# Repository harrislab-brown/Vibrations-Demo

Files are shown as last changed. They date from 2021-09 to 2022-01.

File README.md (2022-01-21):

# Vibrations-Demo
The goal of this project is to create a reconfigurable laboratory kit that is designed to be used as part of a first undergraduate course in mechanical vibrations. The kit was designed to be low-cost and allow for a series of laboratory experiments to be performed remotely. Using a common set of core hardware and software, five laboratory experiments are detailed and can be performed to supplement many of the major topics traditionally encountered in a first vibrations course. 

This repository contains:
1. Assignments: Sample student lab assignments which detail how each demo might be used in the classroom. Each assignment subfolder also contains a video of each demo.
2. CAD files: All files of components needed to be manufactured using 3D printing are provided in both step and stl format. 
3. Laser cut files: All files of components needed to be manufactured by laser cutting are provided in step format.
4. Mechanical drawings: Mechanical drawings of components that need to be manufactured by alternative methods (simple metal working). 
5. Software: All software used in the project (MATLAB GUI, Octave Tone Generator, and Arduino code for accelerometer) are provided. 
6. Vibrations kit assembly guide: A step-by-step guide to assembly and manufacturing of each kit.
7. Vibrations kit BOM: Bill of materials with suggested url for purchasing. 

Additional details on the implementation and motivation can be found at: https://arxiv.org/abs/2110.04668

The documentation in this project is licensed under CC-BY 4.0.
The hardware and software in this project are licensed under CERN-OHL-P.

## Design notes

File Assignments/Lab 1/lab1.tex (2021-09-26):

\documentclass[12pt,letterpaper,english]{article}
\usepackage[T1]{fontenc}
\usepackage[latin9]{inputenc}
\pagestyle{empty}
\usepackage{amsmath}
\usepackage{amssymb}
\usepackage{graphicx}
\usepackage{bm}
\usepackage{multicol}
\usepackage{enumitem}

\usepackage{hyperref}
\hypersetup{
    colorlinks=true,
    linkcolor=blue,
    filecolor=magenta,      
    urlcolor=cyan,
}

\newcommand{\norm}[1]{\lVert#1\rVert}

\makeatletter

\special{papersize=\the\paperwidth,\the\paperheight}

\textwidth6.5in\textheight9in\topmargin-.25in\oddsidemargin0in\evensidemargin0in\parskip5pt\parindent0pt

\usepackage{fancyhdr}
\pagestyle{fancy}
\lhead{Reconfigurable Mechanical Vibrations Laboratory Kit}
\rhead{}

\usepackage{lastpage}

\rfoot{Page \thepage \hspace{1pt} of \pageref{LastPage}}

%\rfoot{\small }
\lfoot{Mechanical Vibrations: Lab 1}

\cfoot{}

\usepackage{babel}

\makeatother

\usepackage{babel}
\begin{document}
\global\long\def\Re{{\rm {Re }}}
 \global\long\def\cL{{\cal L}}
 \global\long\def\sq{{\rm {sq}}}
 \global\long\def\bfx{{\bf x}}
 \global\long\def\bfi{{\bf i}}
 \global\long\def\bfj{{\bf j}}

\begin{center}
\textbf{\large Lab Assignment 1: 1DOF}
\par\end{center}{\large \par}

For this first lab assignment, you will investigate a forced 1 degree of freedom system. The system we will explore is a base excitation problem where a payload is forced by a spring attached to a vibrating base.  Part of the goal of this first assignment will be to help you get familiarized with the shaker setup, housing, and Matlab GUI that will be used for other labs in the future.  

\begin{center}
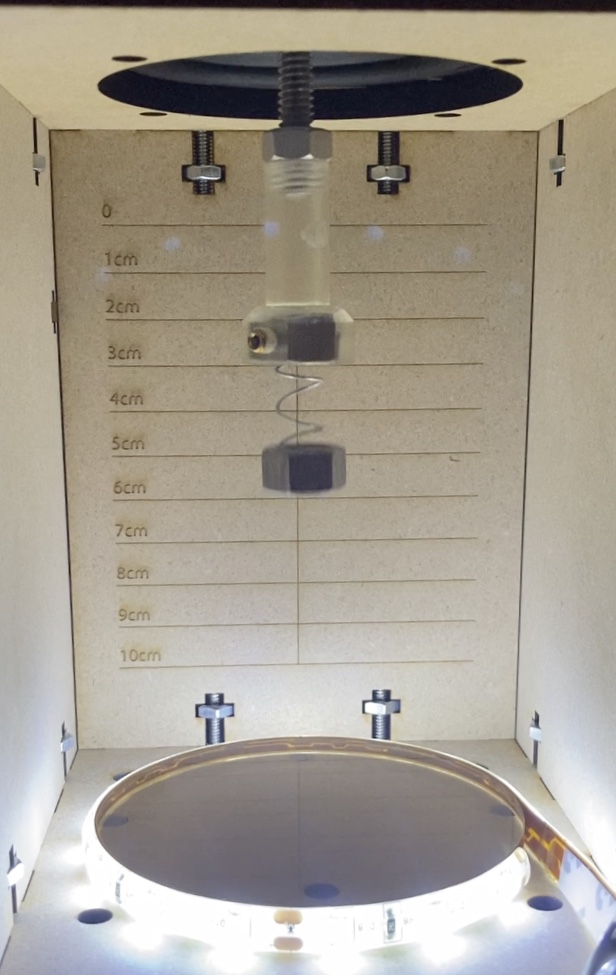
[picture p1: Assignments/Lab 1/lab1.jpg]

\end{center}

\begin{itemize}
\item In the Assembly Guide, first read through and complete the steps in sections A (Housing Assembly), B (Electronics Assembly), C (User Interface), D (Testing the System) to construct the shaker housing, assemble the simple electronic circuit for the shaker and learn to use the GUI.
\item Next read through subsections 1 and 1.1 under section E.  Subsection 1 is a general overview of how to use and assemble parts required for the first demo. Section 1.1 details the specific modifications to the general assembly that are needed for this week's demo. {\it Note that for this demonstration, we will not be using the linear shaft (as described in section E1).}
\end{itemize}

\begin{enumerate}
\item Take a picture of your completed setup.
\item We will first explore the effect of strobing.  For the best effect, the rest of the room should be reasonably dark. To do this, first attach only the nut to the spring (no magnets). Vibrate the speaker at 30Hz with a reasonable amplitude (ensuring that it's not bottoming out!). Then, activate the strobing option on the GUI. Initially, set the strobing frequency offset to 1Hz. Then, explore what happens as the strobing frequency offset is changed to larger or smaller values.  Describe and rationalize observations of the strobing effect you observe and the quantitative influence of the offset.
\item Based on the instructions in E1.1, we will explore the different regimes of forced vibration discussed in class. We will tune the mass of the payload by attaching one or two magnets to the nut. Predict the natural frequency of the three configurations (only nut, one magnet attached, two magnets attached). The spring constant is given by the manufacturer to be around 1050 N/m, while the mass of one nut is approximately 7 g. The mass of one magnet is around 12 g. 
\item We will first investigate the configuration where the nut and one magnet are attached to the end of the spring. Our goal is to use the help of strobing to sweep the frequency space and observe the effect of the driving frequency. For this, we recommend using an offset strobing frequency of 1 or 2 Hz. Start the sweep at around 10 Hz (the speaker is not designed to operate any lower). Then, increase the frequency in 5 Hz steps. As you are doing this, take note of the relative amplitude between the rigid mounting coupler and nut to get a sense of the magnification.  Also take note of the relative phase between the mounting coupler and nut. Continue the sweep in 5 Hz increments until you reach the predicted natural frequency.  You should see the largest amplification around this value since the system is only very weakly damped. Finally sweep beyond the natural frequency until you notice that the nut is almost stationary while the mounting coupler is still visibly vibrating.  Make a qualitative sketch/plot of the motion of the mass and mount as a function of time for three cases (clearly specifying the frequencies chosen): (1) Below the predicted natural frequency, (2) at the predicted natural frequency, and (3) above the natural frequency, again paying particular attention to the relative amplitude and phase of the driving and response.
\begin{itemize} 
\item {\small \underline{Tips:} During the sweep, you may notice that the nut has higher order resonant modes which causes the nut to vibrate side to side. If you encounter these modes, simply skip over that specific frequency (only vertical amplification constitutes the actual resonance we are looking for). 
\item As you sweep, be careful to tune the amplitude slowly so as to avoid the speaker bottoming out (this is when the threading piece glued to the speaker starts hitting the bottom of the speaker and can be easily identified from a clashing sound). As the frequency is increased, the max amplitude of the speaker decreases. Thus you will need to adjust the amplitude value on the GUI as frequency changes. 
\item If the lights start to dim during your sweep, simply reduce the amplitude of the shaker to 0 with the GUI, increase your computer's volume until the lights are at a suitable intensity, then slowly increase the shaker amplitude on the GUI again.
\item If you hear the speaker bottoming out, the fastest way to shutdown the system is to either mute your volume or immediately press the system off button on the GUI. }
\item {\small Ensure that the magnet is properly centered around the nut. This will help minimize any additional side to side vibrational modes. 
\item Be careful when handling the magnets so as to avoid them from snapping together quickly. The best way to remove them from one another once attached is to slide them apart tangentially as opposed to pulling them apart in the normal direction.  }

\end{itemize}

\item Repeat part (d) with no magnet, and finally with both magnets attached. 
\item Provide feedback or ideas (positive and/or areas for improvement) on the setup process and first 1DOF demonstration.  (Optionally) Please also share any other photos or videos you collect!
 
\end{enumerate}

\end{document}

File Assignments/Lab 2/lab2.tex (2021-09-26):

\documentclass[12pt,letterpaper,english]{article}
\usepackage[T1]{fontenc}
\usepackage[latin9]{inputenc}
\pagestyle{empty}
\usepackage{amsmath}
\usepackage{amssymb}
\usepackage{graphicx}
\usepackage{bm}
\usepackage{multicol}
\usepackage{enumitem}

\usepackage{hyperref}
\hypersetup{
    colorlinks=true,
    linkcolor=blue,
    filecolor=magenta,      
    urlcolor=cyan,
}

\newcommand{\norm}[1]{\lVert#1\rVert}

\makeatletter

\special{papersize=\the\paperwidth,\the\paperheight}

\textwidth6.5in\textheight9in\topmargin-.25in\oddsidemargin0in\evensidemargin0in\parskip5pt\parindent0pt

\usepackage{fancyhdr}
\pagestyle{fancy}
\lhead{Reconfigurable Mechanical Vibrations Laboratory Kit}
\rhead{}

\usepackage{lastpage}

\rfoot{Page \thepage \hspace{1pt} of \pageref{LastPage}}

%\rfoot{\small }
\lfoot{Mechanical Vibrations: Lab 2}
\cfoot{}

\usepackage{babel}

\makeatother

\usepackage{babel}
\begin{document}
\global\long\def\Re{{\rm {Re }}}
 \global\long\def\cL{{\cal L}}
 \global\long\def\sq{{\rm {sq}}}
 \global\long\def\bfx{{\bf x}}
 \global\long\def\bfi{{\bf i}}
 \global\long\def\bfj{{\bf j}}

\begin{center}
\textbf{\large Lab Assignment 2: Passive Isolation}
\par\end{center}{\large \par}

Read through section E2 in the Assembly Guide for instructions on what to assemble for this lab. 

First, add about 15 dried beans to the upper platform as shown below.
%
\begin{center}
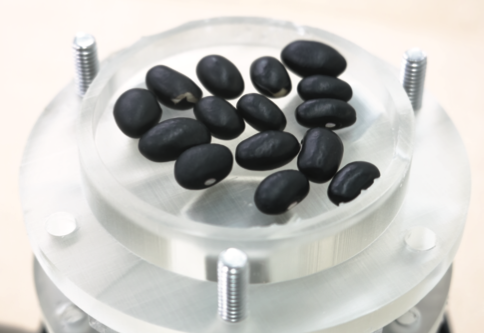
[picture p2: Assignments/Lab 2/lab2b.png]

\end{center}

For this lab, we will explore the effectiveness of a simple passive isolation system. The first configuration (1) contains the upper platform on the passive isolation platform {\it(with the bolts fixed}, shown in the left image below). The second configuration (2) contains the cup placed on the passive isolation rig {\it(without the bolts} so that the springs are free, as in the right image below).

\begin{center}
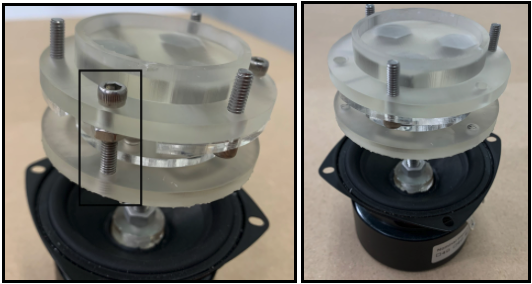
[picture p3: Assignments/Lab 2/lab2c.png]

\end{center}

Set the diving frequency to 120Hz. Note that for the entirety of this demo, the strobing is not needed (but can be experimented with if you would like). Once the shaker starts vibrating, explore configuration (1): rigid support.  Take note of the amplitude at which the beans just begin to move around on the platform. If the amplitude doesn't seem to be high enough, slowly increase the driving amplitude of the speaker until the beans clearly move.  \\

\begin{enumerate}

\item Explore how the intensity of the movement of the beans changes between configuration (1) and (2) under the same driving parameters at 120 Hz.  Take a video of the bean motion for both configurations. 
\item Repeat the above, but this time reducing the driving frequency in 20 Hz steps down to 30 Hz (and resetting the driving amplitude as needed).  
At each frequency, specifically take note as to whether the bean motion appears to be reduced, increased, or stay the same by the inclusion of the springs in configuration (2).  Explain and rationalize your observations.
\begin{itemize}
\item {\small In addition to the bean test, you can also try a ``touch'' test where you gently place your finger on the base and then on the isolation platform.  At each frequency, note how much vibration is transmitted from the base to the isolation platform.}

\end{itemize}

\item Provide feedback or ideas (positive and/or areas for improvement) on the setup process and passive isolation demonstration. 

\end{enumerate}

\end{document}

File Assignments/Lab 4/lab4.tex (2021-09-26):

\documentclass[12pt,letterpaper,english]{article}
\usepackage[T1]{fontenc}
\usepackage[latin9]{inputenc}
\pagestyle{empty}
\usepackage{amsmath}
\usepackage{amssymb}
\usepackage{graphicx}
\usepackage{bm}
\usepackage{multicol}
\usepackage{enumitem}

\usepackage{hyperref}
\hypersetup{
    colorlinks=true,
    linkcolor=blue,
    filecolor=magenta,      
    urlcolor=cyan,
}

\newcommand{\norm}[1]{\lVert#1\rVert}

\makeatletter

\special{papersize=\the\paperwidth,\the\paperheight}

\textwidth6.5in\textheight9in\topmargin-.25in\oddsidemargin0in\evensidemargin0in\parskip5pt\parindent0pt

\usepackage{fancyhdr}
\pagestyle{fancy}
\lhead{Reconfigurable Mechanical Vibrations Laboratory Kit}
\rhead{}

\usepackage{lastpage}

\rfoot{Page \thepage \hspace{1pt} of \pageref{LastPage}}

%\rfoot{\small }
\lfoot{Mechanical Vibrations: Lab 4}
\cfoot{}

\usepackage{babel}

\makeatother

\usepackage{babel}
\begin{document}
\global\long\def\Re{{\rm {Re }}}
 \global\long\def\cL{{\cal L}}
 \global\long\def\sq{{\rm {sq}}}
 \global\long\def\bfx{{\bf x}}
 \global\long\def\bfi{{\bf i}}
 \global\long\def\bfj{{\bf j}}

\begin{center}
\textbf{\large Lab Assignment 4: Multi-DOF Systems}
\par\end{center}{\large \par}

The goal of this demo will be to explore a two degree of freedom system consisting of two springs and two masses. First, read through section E1 (``1 DOF and 2 DOF Assembly'') in the Assembly Guide in order to set up the system.  Note that this setup for this lab is identical to the first lab (1DOF) with the exception of an extra spring and nut added to the assembly. Your final setup should look like the photo below (note that blue guide rod should be attached for this demo for the best results).  

\begin{center}
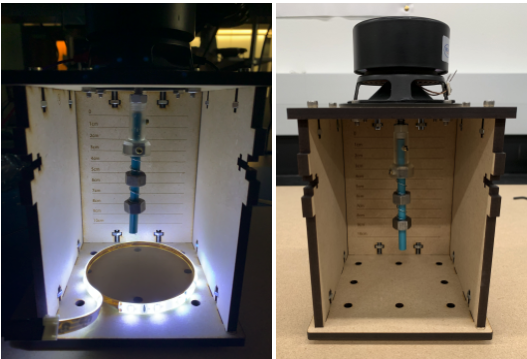
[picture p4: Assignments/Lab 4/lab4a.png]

\end{center}

\begin{enumerate}
\item First, draw a schematic illustrating how you would model the system, labelling all the masses and springs. Note that this can be modeled as a base excitation type problem.  Also clearly label the $x_1$ and $x_2$ coordinates denoting the position of the upper and lower mass, respectively.  
\begin{enumerate}
\item Write down the equations of motion for both masses, then rewrite the system in matrix form. For the purposes of the model, you should assume that the system is undamped, and that the masses and springs are identical.  The spring constant is given by the manufacturer to be around 1050 N/m, while the mass of one nut is approximately 7 g. 
\item Determine the natural frequencies and corresponding mode shapes of the 2DOF system.
\item Lastly, solve for the forced response of the two masses as a function of the driving (i.e. base excitation) frequency.  Plot the frequency response function of the upper mass (mass 1).  Correlate and label the peaks in the frequency response function to the normal modes of the system predicted in the prior part of this problem.  On the same plot, overlay the frequency response function for the 1DOF system from Lab 1 (single spring and nut case).
\item In the 2DOF system, there is also a driving frequency at which the upper mass is predicted to be completely stationary.  Calculate this special frequency.
\end{enumerate}

\item In the experiment, explore driving frequencies from 30Hz to 100Hz in order to experimentally identify the resonant frequencies (and corresponding mode shapes) as well as the special frequency at which the upper mass is nearly stationary.  Setting the strobing frequency to an offset value from the driving frequency will be very helpful for visualizing the relative amplitudes (and for the best effect, turn off the surrounding lights).  Report the experimentally determined frequencies and mode shapes and compare directly to the theoretical predictions from the previous part of this problem.  

\item Lastly, add one additional nut and spring to the end of the chain to create a 3DOF system.  Again by exploring different frequencies under strobing, identify a new qualitative response behavior.  Take a video of one these responses, and include with your assignment.  No calculations are required for this part.

\item Provide feedback or ideas (positive and/or areas for improvement) on the setup process and multi-DOF lab.

\end{enumerate}

\end{document}

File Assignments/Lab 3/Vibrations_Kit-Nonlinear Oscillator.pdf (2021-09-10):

Reconfigurable Mechanical Vibrations Laboratory Kit

### Lab Assignment 3: Nonlinear Oscillator

The goal of this demo will be to investigate the dynamics of a nonlinear oscillator. This system, as depicted below, can be modeled by a Duffing equation where there is a nonlinear spring term in the governing equation.

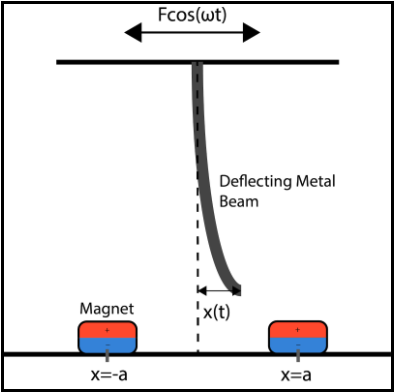
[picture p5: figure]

First, read through section E3 (“Nonlinear Oscillator Demo”) in the Assembly Guide to learn how to modify the existing housing to incorporate the necessary components for this demo. The fully assembled rig should look like this:

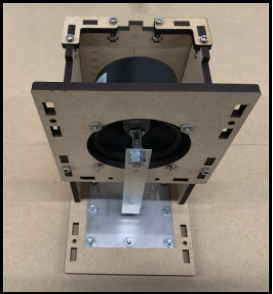
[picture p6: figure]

Note that as detailed in the assembly guide, you will need to add one or two layers of nuts at the bottom of the two magnets such that the height from the top of the beam to the

Mechanical Vibrations: Lab 3 | Page 1 of 4

top surface of the magnets is around 7mm to 7.5mm. (For reference, see the diagram below which includes a way to estimate 7mm using the components of your kit.) Note that the mounting hole on the sheet metal beam has a diameter larger than 1/4”, which also allows additional freedom for fine tuning this spacing. Furthermore, elevating the magnets will make it easier to move the magnets on the steel plate. When placing the magnets, it may be helpful to rotate the beam to an angle so that the magnets do not interact with it. Feel free to add as many nuts as you feel are helpful for stability (see images below).

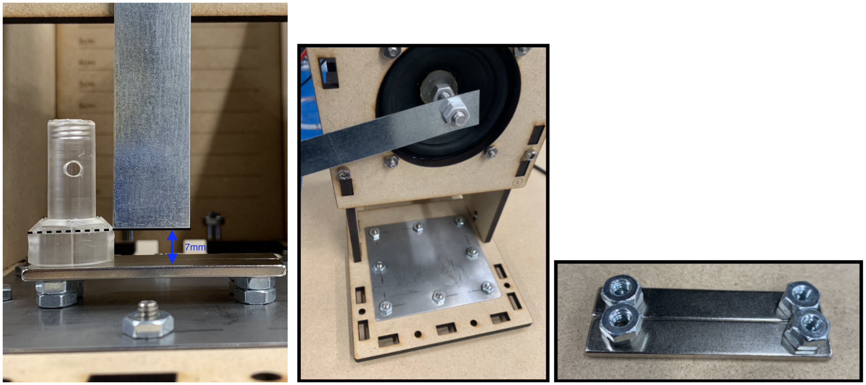
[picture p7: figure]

Next, carefully place the magnets on the steel plate directly below the sheet metal beam. The response of the beam is highly sensitive to the height and location of these magnets. To first ensure that the height of the magnet is suitable (if it is around 7mm to 7.5mm it should be fine), by hand, flick the beam from one equilibrium position to the other as depicted below. You should be able to “feel” the potential well corresponding to each equilibrium position. If you are finding that the beam tends to move away from one equilibrium position, adjust the location of the magnets slightly biasing it towards that particular side.

*Note that we will fine tune the magnets position later on and that this is just to get a sense of the two stable equilibrium positions. Also note that the speaker membrane will deflect as you move the beam.

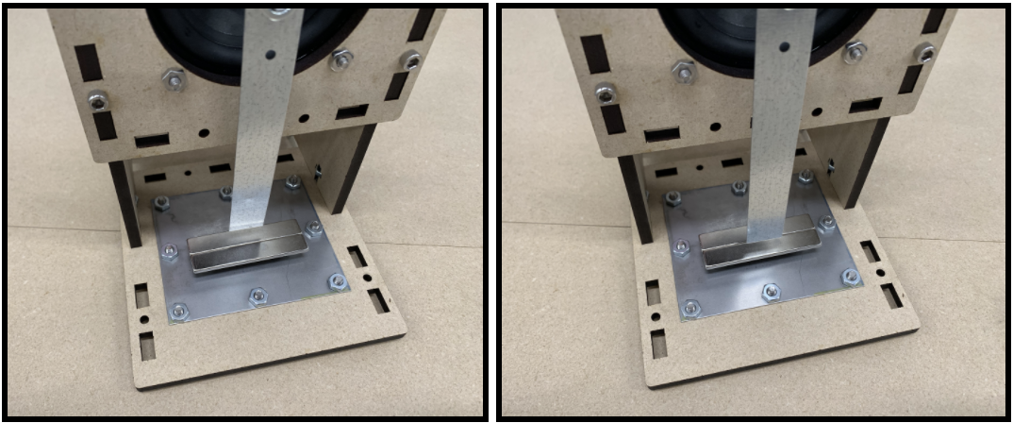
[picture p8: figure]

The motion of the beam can be modeled as a one degree of freedom linear harmonic oscillator where our coordinate of interest is the tip position x(t). Assume the beam has an effective spring constant ks, structural damping coefficient c, and effective mass m.

The additional lateral force that the tip of the beam feels due to the presence of the two magnets can be modeled approximately by the following nonlinear force law

Fm(x) = km

1 −

x
d

2

x

where km ≥ 0 is a parameter that depends on the relative height between the magnets and the beam. For instance, as the magnets are moved further away from the beam km → 0.

1. Write the down the governing ODE for the system, including the magnetic force term Fm. Determine the position of all equilibrium points and their stability as a function of the magnetic parameter km. Describe what happens physically as km is gradually increased starting from 0 (corresponding physically to bringing the magnets closer and closer to the beam).

The equation of motion for this problem has the form of Duffing’s equation, which is a forced nonlinear oscillator that includes a cubic (x

3
) nonlinearity. The general form of the Duffing equation takes the following mathematical form:

x¨ + δx˙ + αx + βx³ = γ cos ωt.

2. Driving the experiment at 20 Hz, slowly increase the driving amplitude (using slightly detuned strobing). You should see three regimes as the amplitude is increased progressively: (1) small oscillations about one of the equilibrium positions, (2) chaotic/irregular oscillation between the two equilibrium positions, (3) large periodic oscillations passing over both equilibrium positions on each cycle. If you do not see these three regimes clearly, you may need to adjust the position of your magnets or the gap between the beam and magnets slightly. Repeat the sweep with the magnets removed to isolate the influence of the magnets (i.e. nonlinearity).

Simulate Duffing’s equation using values δ = 0.5, α = −1, β = 0.2, and ω = 1. By increasing γ generate three phase portraits that correspond qualitatively to the 3 regimes you observe in the experiment. Note that in the simulation there is always an initial transient period before it locks into a specific mode so make sure to run the simulation long enough to discern the steady-state behavior. Include images of the three phase plots (labeled with value of γ used) with your assignment.

3. Now with full freedom on driving frequency and tip spacing, identify another possible qualitative behavior in the experiment. You can use the strobing (synchronized and/or detuned) to help identify the behavior as best as possible. Then similarly with full freedom on the numerical parameters, recover the qualitative mode you observe by simulating Duffing’s equation. Take a video (slo-mo if you have it on your phone) of the new mode and image of the corresponding phase portrait from your simulation to include with your assignment.

4. Provide feedback or ideas (positive and/or areas for improvement) on the setup process and nonlinear oscillation lab.

Application note: A very similar type of “bi-stable system” has been proposed as a method for harvesting energy from mechanical vibration as shown below. The nonlinearity of the system can be exploited to harvest energy effectively over a broader range of frequency input as compared to a linear oscillator which is only effective near its natural frequency. This type of small-scale energy harvester is expected to find applications for powering sensors where another power source cannot be used, such as in implantable devices.

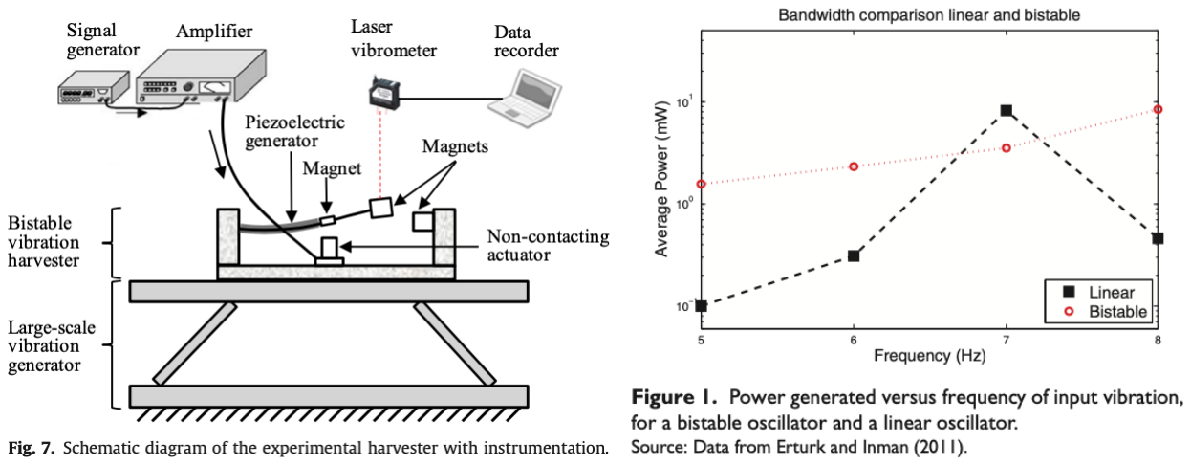
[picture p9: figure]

Figure credit: (left) Zheng, R., Nakano, K., Hu, H., Su, D. and Cartmell, M.P., 2014. An application of stochastic resonance

for energy harvesting in a bistable vibrating system. Journal of Sound and Vibration, 333(12), pp.2568-2587. (right) Pellegrini,

S.P., Tolou, N., Schenk, M. and Herder, J.L., 2013. Bistable vibration energy harvesters: a review. Journal of Intelligent

Material Systems and Structures, 24(11), pp.1303-1312.

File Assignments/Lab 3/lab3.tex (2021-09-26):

\documentclass[12pt,letterpaper,english]{article}
\usepackage[T1]{fontenc}
\usepackage[latin9]{inputenc}
\pagestyle{empty}
\usepackage{amsmath}
\usepackage{amssymb}
\usepackage{graphicx}
\usepackage{bm}
\usepackage{multicol}
\usepackage{enumitem}

\usepackage{hyperref}
\hypersetup{
    colorlinks=true,
    linkcolor=blue,
    filecolor=magenta,      
    urlcolor=cyan,
}

\newcommand{\norm}[1]{\lVert#1\rVert}

\makeatletter

\special{papersize=\the\paperwidth,\the\paperheight}

\textwidth6.5in\textheight9in\topmargin-.25in\oddsidemargin0in\evensidemargin0in\parskip5pt\parindent0pt

\usepackage{fancyhdr}
\pagestyle{fancy}
\lhead{Reconfigurable Mechanical Vibrations Laboratory Kit}
\rhead{}

\usepackage{lastpage}

\rfoot{Page \thepage \hspace{1pt} of \pageref{LastPage}}

%\rfoot{\small }
\lfoot{Mechanical Vibrations: Lab 3}
\cfoot{}

\usepackage{babel}

\makeatother

\usepackage{babel}
\begin{document}
\global\long\def\Re{{\rm {Re }}}
 \global\long\def\cL{{\cal L}}
 \global\long\def\sq{{\rm {sq}}}
 \global\long\def\bfx{{\bf x}}
 \global\long\def\bfi{{\bf i}}
 \global\long\def\bfj{{\bf j}}

\begin{center}
\textbf{\large Lab Assignment 3:  Nonlinear Oscillator}
\par\end{center}{\large \par}

The goal of this demo will be to investigate the dynamics of a nonlinear oscillator.  This system, as depicted below, can be modeled by a Duffing equation where there is a nonlinear spring term in the governing equation.

\begin{center}

\end{center}

First, read through section E3 (``Nonlinear Oscillator Demo'') in the Assembly Guide to learn how to modify the existing housing to incorporate the necessary components for this demo. The fully assembled rig should look like this:

\begin{center}

\end{center}

Note that as detailed in the assembly guide, you will need to add one or two layers of nuts at the bottom of the two magnets such that the height from the top of the beam to the top surface of the magnets is around 7mm to 7.5mm. (For reference, see the diagram below which includes a way to estimate 7mm using the components of your kit.)  Note that the mounting hole on the sheet metal beam has a diameter larger than 1/4'', which also allows additional freedom for fine tuning this spacing. Furthermore, elevating the magnets will make it easier to move the magnets on the steel plate. When placing the magnets, it may be helpful to rotate the beam to an angle so that the magnets do not interact with it. Feel free to add as many nuts as you feel are helpful for stability (see images below). 

\begin{center}
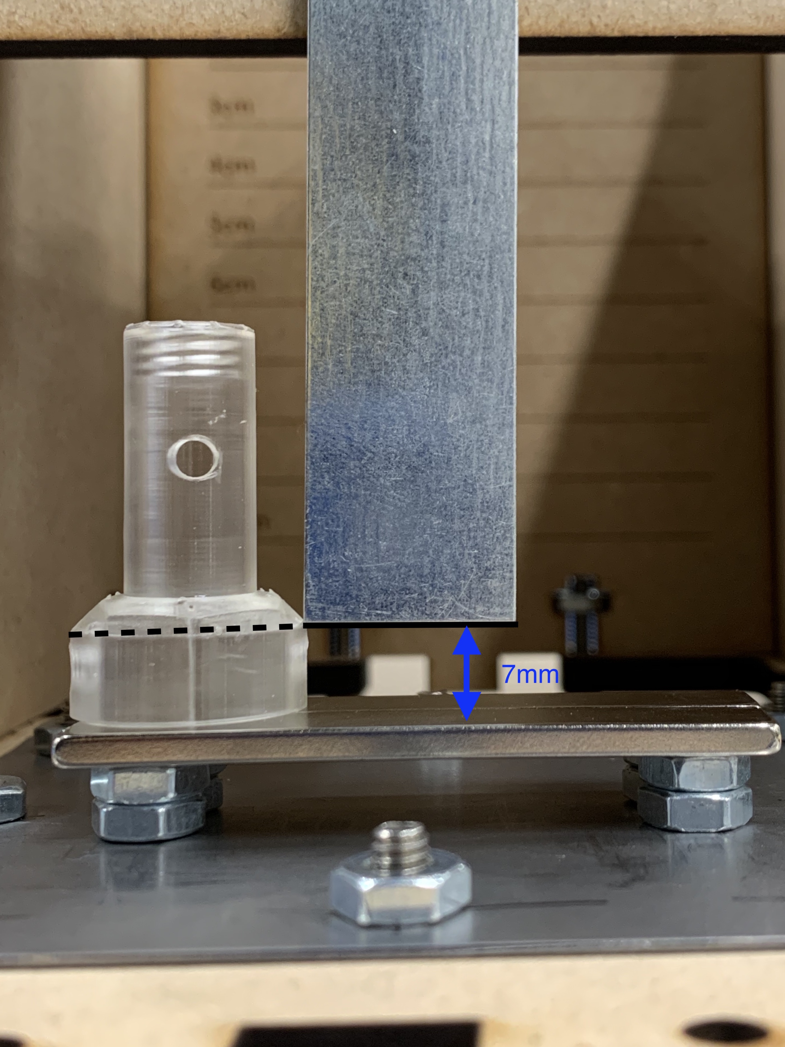
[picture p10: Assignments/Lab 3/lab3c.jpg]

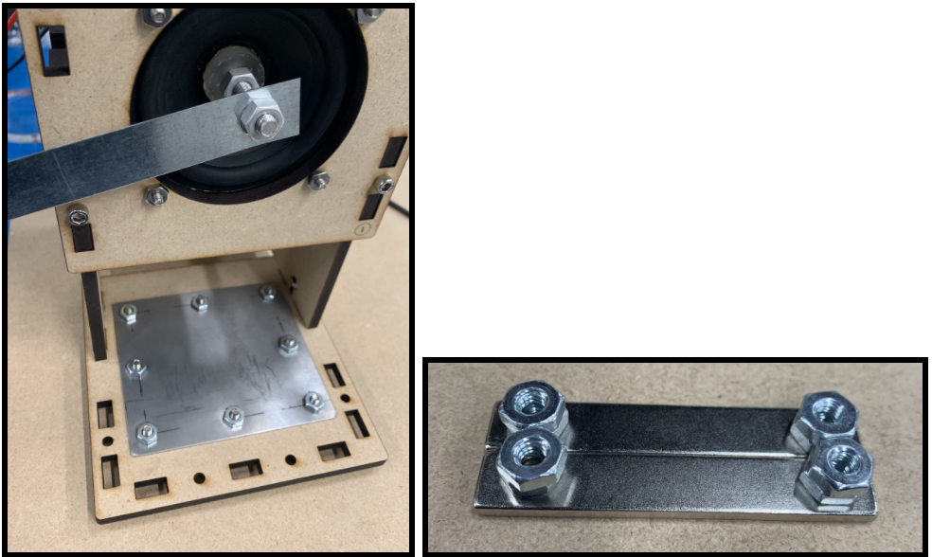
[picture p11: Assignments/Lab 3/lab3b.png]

\end{center}

Next, carefully place the magnets on the steel plate directly below the sheet metal beam. The response of the beam is highly sensitive to the height and location of these magnets. To first ensure that the height of the magnet is suitable (if it is around 7mm to 7.5mm it should be fine), by hand, flick the beam from one equilibrium position to the other as depicted below. You should be able to ``feel'' the potential well corresponding to each equilibrium position. If you are finding that the beam tends to move away from one equilibrium position, adjust the location of the magnets slightly biasing it towards that particular side. 

{\small *Note that we will fine tune the magnets position later on and that this is just to get a sense of the two stable equilibrium positions.  Also note that the speaker membrane will deflect as you move the beam.}

\begin{center}
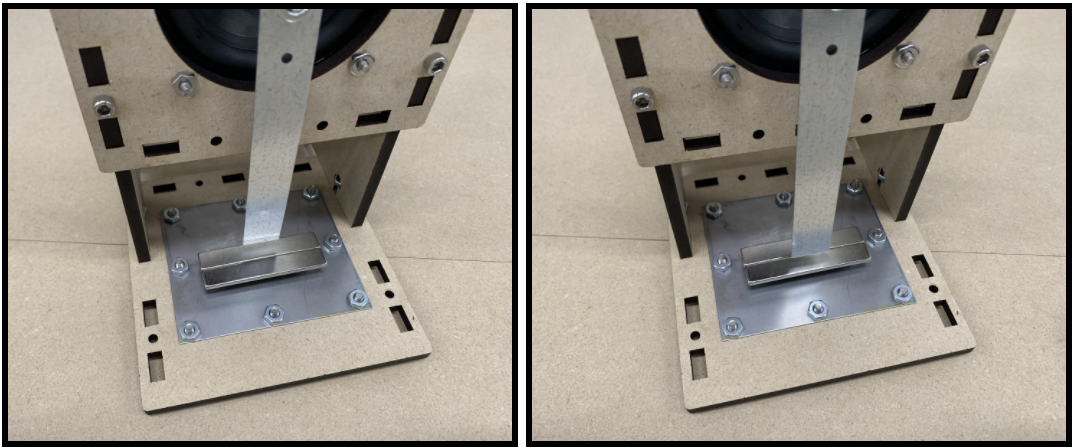
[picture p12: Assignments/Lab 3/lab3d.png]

\end{center}

The motion of the beam can be modeled as a one degree of freedom linear harmonic oscillator where our coordinate of interest is the tip position $x(t)$.  Assume the beam has an effective spring constant $k_s$, structural damping coefficient $c$, and effective mass $m$.

The additional lateral force that the tip of the beam feels due to the presence of the two magnets can be modeled approximately by the following nonlinear force law
\begin{equation}
F_m(x)=k_m \left[1-\left(\frac{x}{d}\right)^2\right]x \nonumber
\end{equation}
where $k_m\geq0$ is a parameter that depends on the relative height between the magnets and the beam.  For instance, as the magnets are moved further away from the beam $k_m \rightarrow 0$.

\begin{enumerate}
\item Write the down the governing ODE for the system, including the magnetic force term $F_m$.  Determine the position of all equilibrium points and their stability as a function of the magnetic parameter $k_m$.  Describe what happens physically as $k_m$ is gradually increased starting from 0 (corresponding physically to bringing the magnets closer and closer to the beam).
\end{enumerate}

The equation of motion for this problem has the form of Duffing's equation, which is a forced nonlinear oscillator that includes a cubic ($x^3$) nonlinearity.  The general form of the Duffing equation takes the following mathematical form:
\begin{equation}
\ddot{x}+\delta \dot{x} +\alpha x + \beta x^3 = \gamma \cos \omega t \nonumber.
\end{equation}
\begin{enumerate}[resume]
\item Driving the experiment at 20 Hz, slowly increase the driving amplitude (using slightly detuned strobing).  You should see three regimes as the amplitude is increased progressively: (1) small oscillations about one of the equilibrium positions, (2) chaotic/irregular oscillation between the two equilibrium positions, (3) large \emph{periodic} oscillations passing over both equilibrium positions on each cycle.  If you do not see these three regimes clearly, you may need to adjust the position of your magnets or the gap between the beam and magnets slightly.  Repeat the sweep with the magnets removed to isolate the influence of the magnets (i.e. nonlinearity).

\vspace{0.05in}

Simulate Duffing's equation using values $\delta=0.5$, $\alpha=-1$, $\beta = 0.2$, and $\omega=1$.  By increasing $\gamma$ generate three phase portraits that correspond qualitatively to the 3 regimes you observe in the experiment.  Note that in the simulation there is always an initial \emph{transient} period before it locks into a specific mode so make sure to run the simulation long enough to discern the steady-state behavior.  Include images of the three phase plots (labeled with value of $\gamma$ used) with your assignment.

\item Now with full freedom on driving frequency and tip spacing, identify another possible \emph{qualitative} behavior in the experiment.  You can use the strobing (synchronized and/or detuned) to help identify the behavior as best as possible.  Then similarly with full freedom on the numerical parameters, recover the qualitative mode you observe by simulating Duffing's equation.  Take a video (slo-mo if you have it on your phone) of the new mode and image of the corresponding phase portrait from your simulation to include with your assignment.

\item Provide feedback or ideas (positive and/or areas for improvement) on the setup process and nonlinear oscillation lab. 

\end{enumerate}

\vspace{0.5 in}

{\it \small Application note: A very similar type of ``bi-stable system'' has been proposed as a method for harvesting energy from mechanical vibration as shown below. The nonlinearity of the system can be exploited to harvest energy effectively over a broader range of frequency input as compared to a linear oscillator which is only effective near its natural frequency.  This type of small-scale energy harvester is expected to find applications for powering sensors where another power source cannot be used, such as in implantable devices.}

\begin{center}
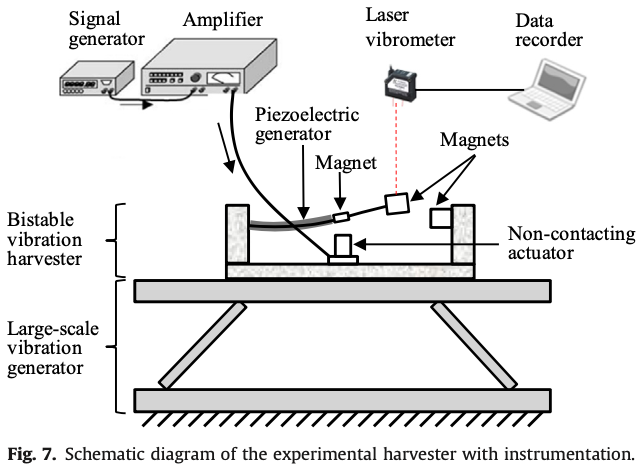
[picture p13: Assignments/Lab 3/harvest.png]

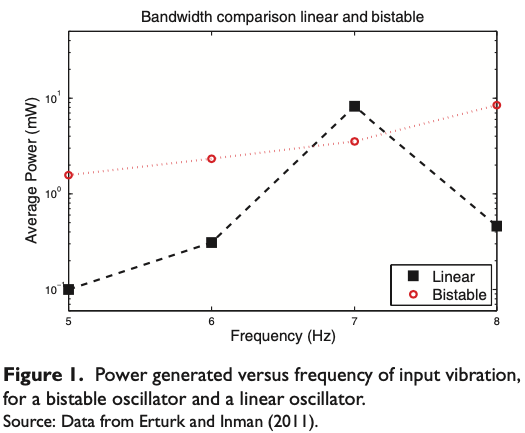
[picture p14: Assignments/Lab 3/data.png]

\end{center}

{\it \scriptsize	 Figure credit: (left) Zheng, R., Nakano, K., Hu, H., Su, D. and Cartmell, M.P., 2014. An application of stochastic resonance for energy harvesting in a bistable vibrating system. Journal of Sound and Vibration, 333(12), pp.2568-2587.  (right) Pellegrini, S.P., Tolou, N., Schenk, M. and Herder, J.L., 2013. Bistable vibration energy harvesters: a review. Journal of Intelligent Material Systems and Structures, 24(11), pp.1303-1312. }

\end{document}

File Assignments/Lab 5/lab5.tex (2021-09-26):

\documentclass[12pt,letterpaper,english]{article}
\usepackage[T1]{fontenc}
\usepackage[latin9]{inputenc}
\pagestyle{empty}
\usepackage{amsmath}
\usepackage{amssymb}
\usepackage{graphicx}
\usepackage{bm}
\usepackage{multicol}
\usepackage{enumitem}

\usepackage{hyperref}
\hypersetup{
    colorlinks=true,
    linkcolor=blue,
    filecolor=magenta,      
    urlcolor=cyan,
}

\newcommand{\norm}[1]{\lVert#1\rVert}

\makeatletter

\special{papersize=\the\paperwidth,\the\paperheight}

\textwidth6.5in\textheight9in\topmargin-.25in\oddsidemargin0in\evensidemargin0in\parskip5pt\parindent0pt

\usepackage{fancyhdr}
\pagestyle{fancy}
\lhead{Reconfigurable Mechanical Vibrations Laboratory Kit}
\rhead{}

\usepackage{lastpage}

\rfoot{Page \thepage \hspace{1pt} of \pageref{LastPage}}

%\rfoot{\small }
\lfoot{Mechanical Vibrations: Lab 5}
\cfoot{}

\usepackage{babel}

\makeatother

\usepackage{babel}
\begin{document}
\global\long\def\Re{{\rm {Re }}}
 \global\long\def\cL{{\cal L}}
 \global\long\def\sq{{\rm {sq}}}
 \global\long\def\bfx{{\bf x}}
 \global\long\def\bfi{{\bf i}}
 \global\long\def\bfj{{\bf j}}

\begin{center}
\textbf{\large Lab Assignment 5: Continuous Systems}
\par\end{center}{\large \par}

The goal of this demo will be to investigate the resonant modes of a tensioned string under harmonic forcing. We will explore how the resonant frequencies are related to the string's tension and length. First, read through section E4 (``String-Wave Assembly'') in the Assembly Guide in order to set up the system.
\begin{center}
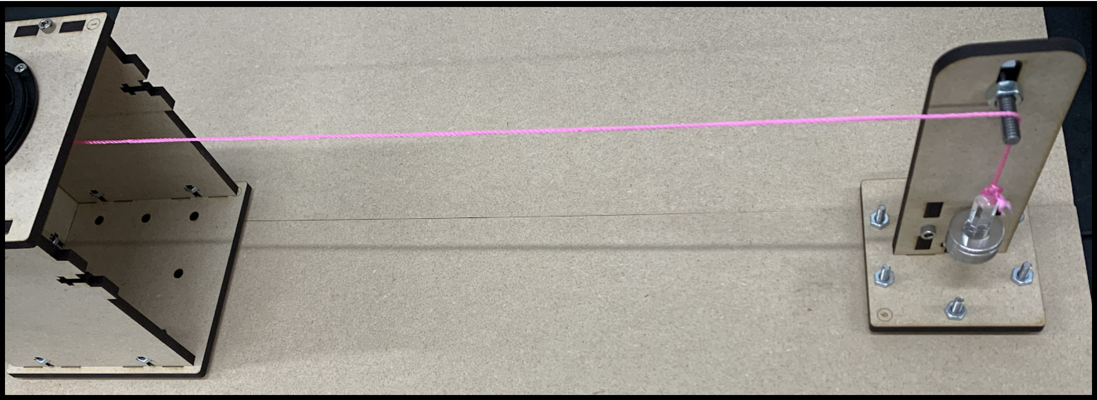
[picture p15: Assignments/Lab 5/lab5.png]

\end{center}

Cut the string into a longer section and a shorter section. We recommend that the `long' string be smaller or equal to approximately an arms length ($\sim$60cm) and the `short' string be around 30-40cm for good results.  Place the LED lights at the center of the string for strobing.

 %(this is to ensure that the fundamental mode is at least 20Hz, the minimum frequency at which the vibration of the speaker is reasonably uniform).  

\begin{enumerate}
\item To model this system, we will assume the string of length $L$ is under a constant tension $T$ that has constant linear density $\rho$.  In class, we saw that this physical system can be modeled by the PDE
\begin{equation}
\frac{\partial^2 u}{\partial t^2} = \frac{T}{\rho}\frac{\partial^2 u}{\partial x^2}. \nonumber
\end{equation}
In our lab, one end is shaken harmonically with amplitude $u(x=0,t)=a \cos{\omega t}$, and the other end is held fixed such that $u(x=L,t)=0$.  In the steps below we will seek the steady-state solution to the problem, ignoring any transients, and interpret the solution.

\begin{enumerate}
\item Since the problem is undamped and linear, we first make a guess of the steady-state solution of the form: $u(x,t)=f(x)\cos{\omega t}$.  By substituting our guess into the governing PDE, find an ODE for $f(x)$.  Solve the ODE and construct the form of $u(x,t)$.  You should still have two undetermined variables at this point.
\item Using appropriate boundary conditions, solve for the undetermined coefficients to find the steady-state solution for $u(x,t)$.  Plot the amplitude of the response as a function of the driving frequency $\omega$.
\item Using your expression for the steady-state solution, find the frequencies at which the amplitude is predicted to diverge (e.g. the resonant frequencies).  Compare your result to the natural frequencies of the equivalent free problem solved in class.
\item Reinterpret your result from the prior part in terms of the timescales in the problem. 

{\it \small Hint: Recall that we can interpret $c=\sqrt{T/\rho}$ as a wave speed in this problem.  First compute the time it takes for a wave to travel the length $L$ of the string.}
\end{enumerate}
\item Move on to the experiment.  Mount the longer string on the setup and place a total of 10 washers on the T-piece. Measure (approximately) the length of the string starting from the base of the shaker to the contact point with the screw at the string mount. We will investigate how the tension in the string affects the frequency at which each resonance occurs. If you are finding the string mount to be unstable, you can try taping it down or adding additional weight to its base.
\begin{enumerate}
\item Sweep through frequencies starting at around 10Hz (if the length is around an arms length), and identify the frequencies at which you experimentally observe the first 3 harmonic modes.  Sketch each of the modes and label them with their experimental natural frequency.
\item Repeat the same test but this time change the tension of the string by either adding weights (you can add some of the 3/8'' nuts) or removing some washers. Note that you want to change the mass by at least roughly $\sim$15g to most clearly observe the effects of changing tension.  Once again sweep through a range of frequencies to identify the frequencies at which the first 3 resonant modes occur.
\item The mass of one washer is 2.75g, while the mass of the T-piece is 2.6g. Use the expressions derived in the first part of this problem to predict the ratio of the original fundamental resonant frequency (10 washers) and the new fundamental resonant frequency (after having changed the mass). Then, calculate the ratio between the corresponding values that were determined experimentally and compare to your theoretical prediction. 

{\small \it Note: You may find it easier to identify the second resonant mode as compared to the fundamental mode. As such, you can alternatively predict and measure the ratios using this second mode instead.}
% Also note that during intermediate regimes, you will notice a combination of several harmonics, this is a good way to determine where the different modes are. Another way is to note at what frequency the modes clearly transition and to use that as a guide.
\end{enumerate}
\item Next, switch the mounted string to the shorter piece and place a total of 10 washers on the T-piece. Measure (approximately) the length of the string starting from the base of the shaker to the contact point. 
\begin{enumerate}
\item Repeat the frequency sweep to determine the approximate frequencies for the first 3 resonant modes. 
\item Next, based on the measured lengths of each string, calculate the ratio between the old fundamental frequency (long string) and the new fundamental frequency (short string). Then, calculate this ratio from the experimentally determined values. Compare the results.
\end{enumerate}

\item For any of the configurations described above, take a single still photograph of each resonant modes you can observe.  Combine these into a single image to include with your assignment.  No calculations are required for this part.

\item Provide feedback or ideas (positive and/or areas for improvement) on the setup process and continuous system lab.

\end{enumerate}

\end{document}

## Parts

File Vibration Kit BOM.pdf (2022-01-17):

Item | Manufacturer | Price per unit | # Per unit sold | # Per set needed | Link | Subsystem
Speaker | DROK | 17.95 | 1 | 1 | https://www.amazon.com/DROK-Antimagnetic-Full-Range-Interference-Loudspeaker/dp/B01IN8YI4Y/ref=sr_1_3?crid=168FILK7GKQZ8&dchild=1&keywords=drok+3+inch+speaker&qid=1597640468&sprefix=Drok+3+inch+%2Caps%2C154&sr=8-3 (https://www.amazon.com/DROK-Antimagnetic-Full-Range-Interference-Loudspeaker/dp/B01IN8YI4Y)
Amp | Facmogu | 18.99 | 2 | 1 | https://www.amazon.com/dp/B075CBHZW9/ref=dp_cerb_3
12V Power Supply | SmoTecQ | 12.99 | 2 | 1 | https://www.amazon.com/100-240V-Transformers-Switching-Applications-Connectors/dp/B077PW5JC3/ref=sr_1_3?dchild=1&keywords=power+supply+12v&qid=1597667751&sr=8-3 (https://www.amazon.com/100-240V-Transformers-Switching-Applications-Connectors/dp/B077PW5JC3)
Aux Cable | JXMOX | 7.99 | 2 | 1 | https://www.amazon.com/Oldboytech-Auxiliary-Braided-Compatible-Headphones/dp/B076BFZDG2/ref=sr_1_2_sspa?dchild=1&keywords=aux%2Bcable&qid=1597640754&sr=8-2-spons&spLa=ZW5jcnlwdGVkUXVhbGlmaWVyPUExOVhI MTFFSUJMSzQzJmVuY3J5cHRlZElkPUEwMTkzNzIzUTJ GN1RLNlFDOUg1JmVuY3J5cHRlZEFkSWQ9QTA2MDk3 NThWMzM3VkZMQk01WDImd2lkZ2V0TmFtZT1zcF9hdG YmYWN0aW9uPWNsaWNrUmVkaXJlY3QmZG9Ob3RMb 2dDbGljaz10cnVl&th=1 (https://www.amazon.com/Oldboytech-Auxiliary-Braided-Compatible-Headphones/dp/B076BFZDG2)
Alligator Clip Test Leads | ELEGOO | 8.99 | 30 | 2 | https://www.amazon.com/Alligator-Leads-ELEGOO-Double-end-Jumper/dp/B0739YWFQ6 (https://www.amazon.com/Alligator-Leads-ELEGOO-Double-end-Jumper/dp/B0739YWFQ6)
Wires | Hellotronics Jumper Wires | 13.99 | 120 | 6 | https://www.amazon.com/Breadboard-20-More-Red-Black-Jumpers-120-Pack-Hellotronics/dp/B07XMG9LSZ/ref=sr_1_2_sspa?dchild=1&keywords=Arduino%2Bmale%2Bto%2Bmale%2Bjumper%2Bwire&qid=1597563563&sr=8-2-spons&spLa=ZW5jcnlwdGVkUXVhbGlmaWVyPUExMFMz MEVXMDM1M0hQJmVuY3J5cHRlZElkPUEwODI4MDU5 MUU5MEY2QVhWMzlTTyZlbmNyeXB0ZWRBZElkPUEwN DkxNjI4MVAwWVA2RFdPRThMJndpZGdldE5hbWU9c3Bf YXRmJmFjdGlvbj1jbGlja1JlZGlyZWN0JmRvTm90TG9nQ2

Shaker

xpY2s9dHJ1ZQ&th=1 (https://www.amazon.com/Breadboard-20-More-Red-Black-Jumpers-120-Pack-Hellotronics/dp/B07XMG9LSZ)

Lights | GuoTonG | 11.99 | 16 | 1.9

https://www.amazon.com/GuoTonG-Flexible-Waterproof-Ribbon-Lighting/dp/B075LB9HK2/ref=sr_1_1_sspa?crid=2PC30TPDVRZYY&dchild=1&keywords=flexible%2Bled%2Bstrip%2Blights%
2Bwhite&qid=1597565009&sprefix=flexible%2Bled% 2Bstrip%2Blights%2Bno%2Bwhy%2Caps%2C155&sr=8-1-spons&spLa=ZW5jcnlwdGVkUXVhbGlmaWVyPUE3VjRH WkwwSjg1WlcmZW5jcnlwdGVkSWQ9QTA3NTYxNDUxR0 FSTE5MWTdNVEswJmVuY3J5cHRlZEFkSWQ9QTAzMjU 3MTEyMjFMNkhQQU5UMDlCJndpZGdldE5hbWU9c3BfY XRmJmFjdGlvbj1jbGlja1JlZGlyZWN0JmRvTm90TG9nQ2x pY2s9dHJ1ZQ&th=1 (https://www.amazon.com/GuoTonG-Flexible-Waterproof-Ribbon-Lighting/dp/B075LB9HK2)

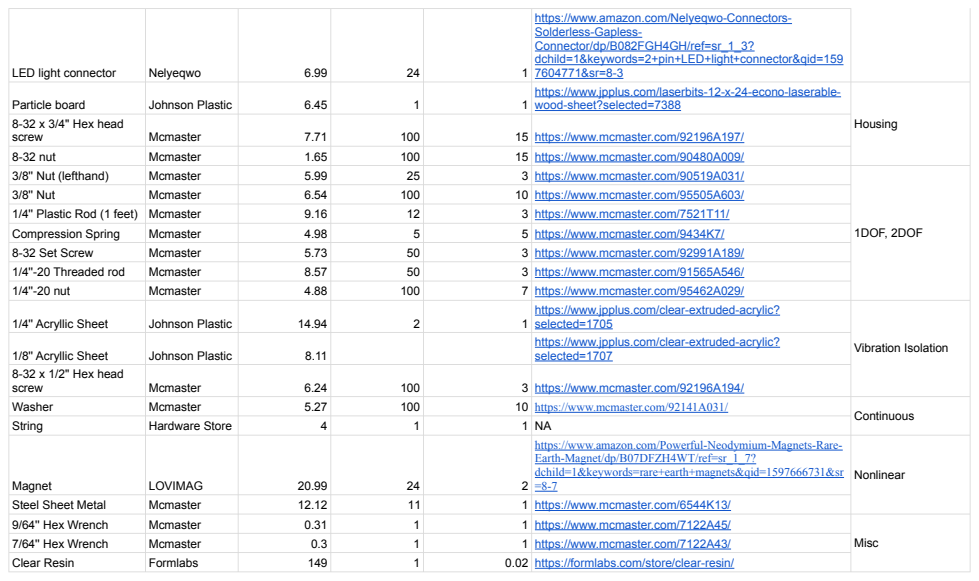
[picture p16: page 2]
LED light connector; Nelyeqwo; Particle board; Johnson Plastic; 8-32 x 3/4'' Hex head; Housing; screw; Mcmaster; 15 https://www.mcmaster.com/92196A197/; 8-32 nut; 15 https://www.mcmaster.com/90480A009/; 3/8'' Nut (lefthand); 3 https://www.mcmaster.com/90519A031/; 1DOF, 2DOF; 3/8'' Nut; 10 https://www.mcmaster.com/95505A603/; 1/4'' Plastic Rod (1 feet) Mcmaster; 3 https://www.mcmaster.com/7521T11/; Compression Spring; 5 https://www.mcmaster.com/9434K7/; 8-32 Set Screw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

https://www.amazon.com/Nelyeqwo-Connectors-
Solderless-Gapless-
Connector/dp/B082FGH4GH/ref=sr_1_3?
dchild=1&keywords=2+pin+LED+light+connector&qid=159
https://www.jpplus.com/laserbits-12-x-24-econo-laserable-
wood-sheet?selected=7388 (https://www.jpplus.com/laserbits-12-x-24-econo-laserable-wood-sheet?selected=7388)

https://www.jpplus.com/clear-extruded-acrylic?
selected=1705 (https://www.jpplus.com/clear-extruded-acrylic?selected=1705)
selected=1707 (https://www.jpplus.com/clear-extruded-acrylic?selected=1707)

https://www.amazon.com/Powerful-Neodymium-Magnets-Rare-
Earth-Magnet/dp/B07DFZH4WT/ref=sr_1_7?
dchild=1&keywords=rare+earth+magnets&qid=1597666731&sr

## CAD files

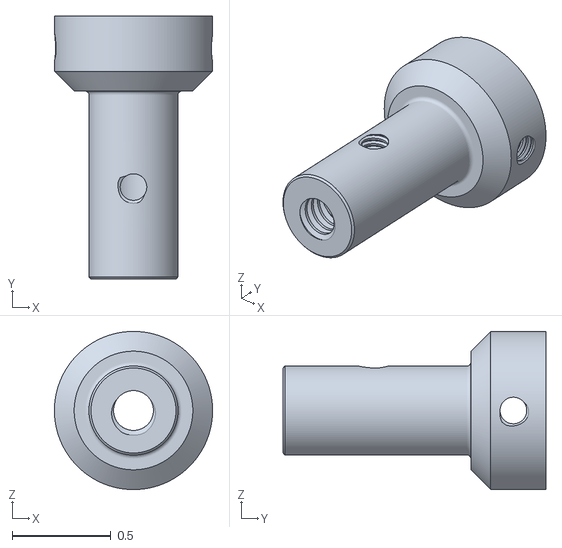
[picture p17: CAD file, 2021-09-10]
CAD files/1DOF,2DOF/Custom Mount.stl
0.8 x 1.33 x 0.8

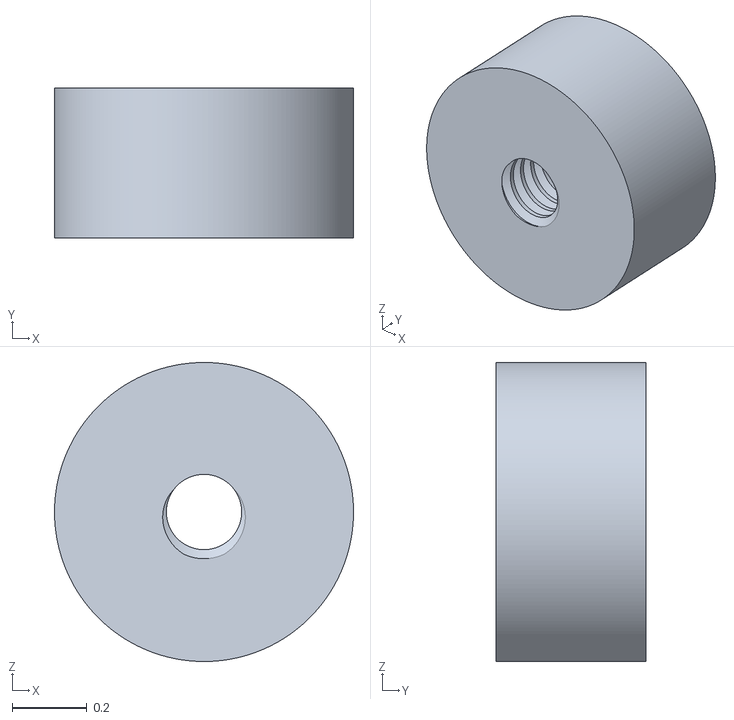
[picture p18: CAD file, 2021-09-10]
CAD files/Shaker/Cylinder mount.stl
0.8 x 0.4 x 0.8

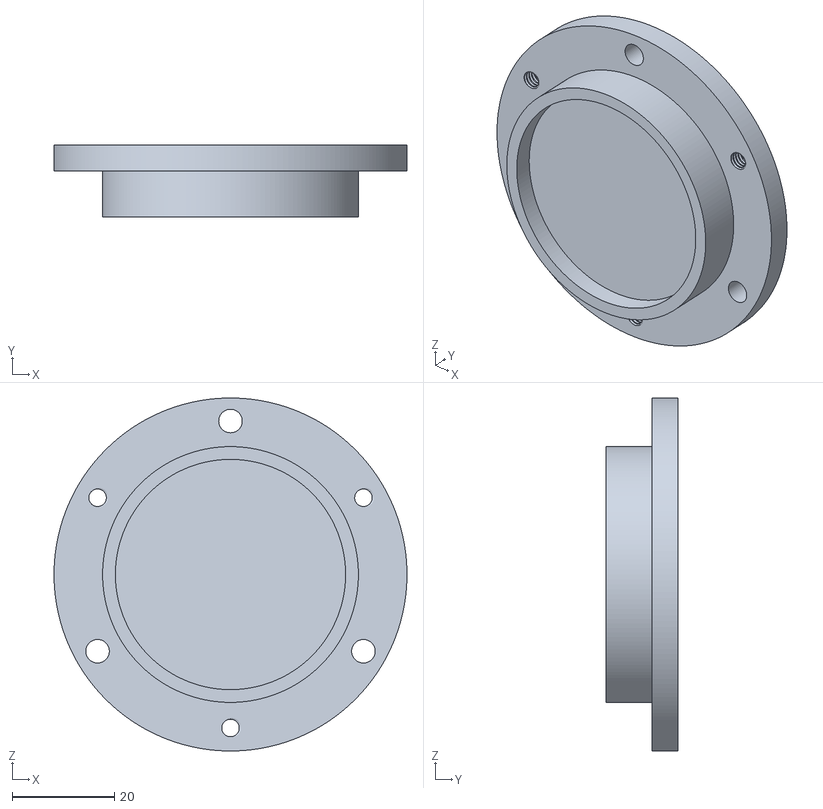
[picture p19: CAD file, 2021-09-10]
CAD files/Vibration Isolation/top platform.stl
69.0 x 14.0 x 69.0

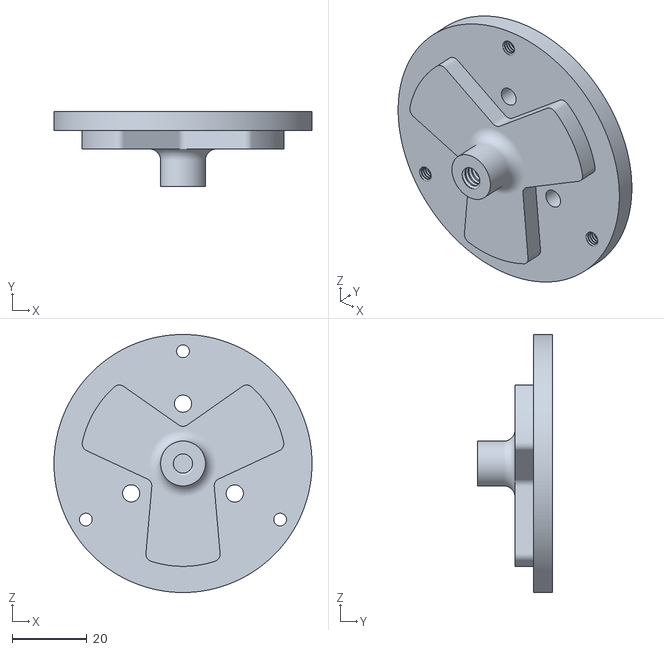
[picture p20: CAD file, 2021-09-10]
CAD files/Vibration Isolation/bottom platform.stl
69.0 x 20.0 x 69.0

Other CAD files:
CAD files/1DOF,2DOF/Custom Mount.f3d
CAD files/Shaker/Cylinder mount.f3d
CAD files/Vibration Isolation/bottom platform.f3d
CAD files/Vibration Isolation/top platform.f3d

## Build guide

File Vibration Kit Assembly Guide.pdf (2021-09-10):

### Demo Kit Assembly Guide

(A) Housing Assembly | 2
(B) Electronics Assembly | 5
(C) User Interface | 12
(D) Testing the UI with the Speaker and Lighting | 17
(E) Experiments | 18
(1) 1 DOF and 2 DOF Assembly | 18
(1.1) Alternative assembly for use with magnet (1DOF HW): | 23
(2) Vibration Isolation Assembly | 25
(3) Nonlinear Oscillator Assembly | 30
(4) String-Wave Assembly | 35
(F) Manufacturing Steps | 48

## Warning: Use of the LED strobing for the activities described in this document is strictly optional. Do not connect the lighting system if you have any

sensitivity to flashing lights.

## (A) Housing Assembly

Materials:

Number | Item | Quantity
1 | Top Plate | 1
2 | Left Plate | 1
3 | Right Plate | 1
4 | Back Plate | 1
5 | Base Plate | 1
6 | 8-32 x 3/4'' Hex head screw | 12
7 | 8-32 Hex nut | 12
8 | 9/64'' Allen Key | 1

Assembly Steps:
1) Mount the Left Plate (2), Right Plate (3), and Back Plate (4) on the Base Plate (5) by inserting the rectangular extrusions into the corresponding slots.

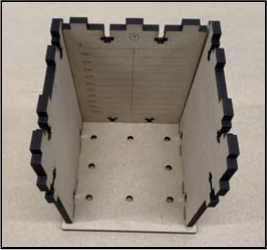
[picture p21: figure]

2) Mount the Top Plate (1), once again making sure the slots are aligned.

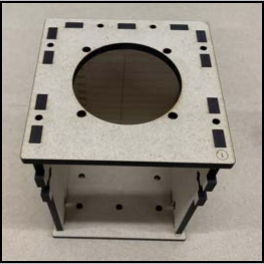
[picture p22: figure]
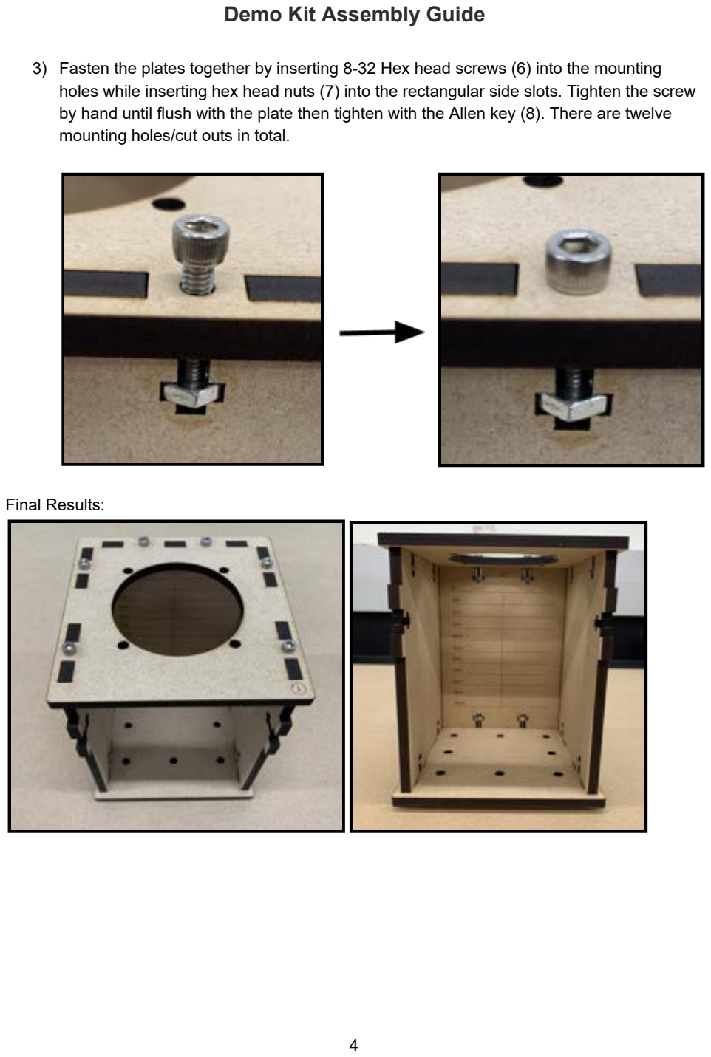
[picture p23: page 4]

3) Fasten the plates together by inserting 8-32 Hex head screws (6) into the mounting holes while inserting hex head nuts (7) into the rectangular side slots. Tighten the screw by hand until flush with the plate then tighten with the Allen key (8). There are twelve mounting holes/cut outs in total.

Final Results:

## (B) Electronics Assembly

Materials:

Number | Item | Quantity
1 | 12V Power Supply | 1
2 | Amplifier | 2
3 | Aux Cable | 1
4 | Jumper Wire (with LED strip connector) | 1
5 | Jumper Wires | 4
6 | LED Lights (with Acrylic disk) | 1
7 | Alligator Clips | 2
8 | Speaker | 1
9 | Screw Driver | 1

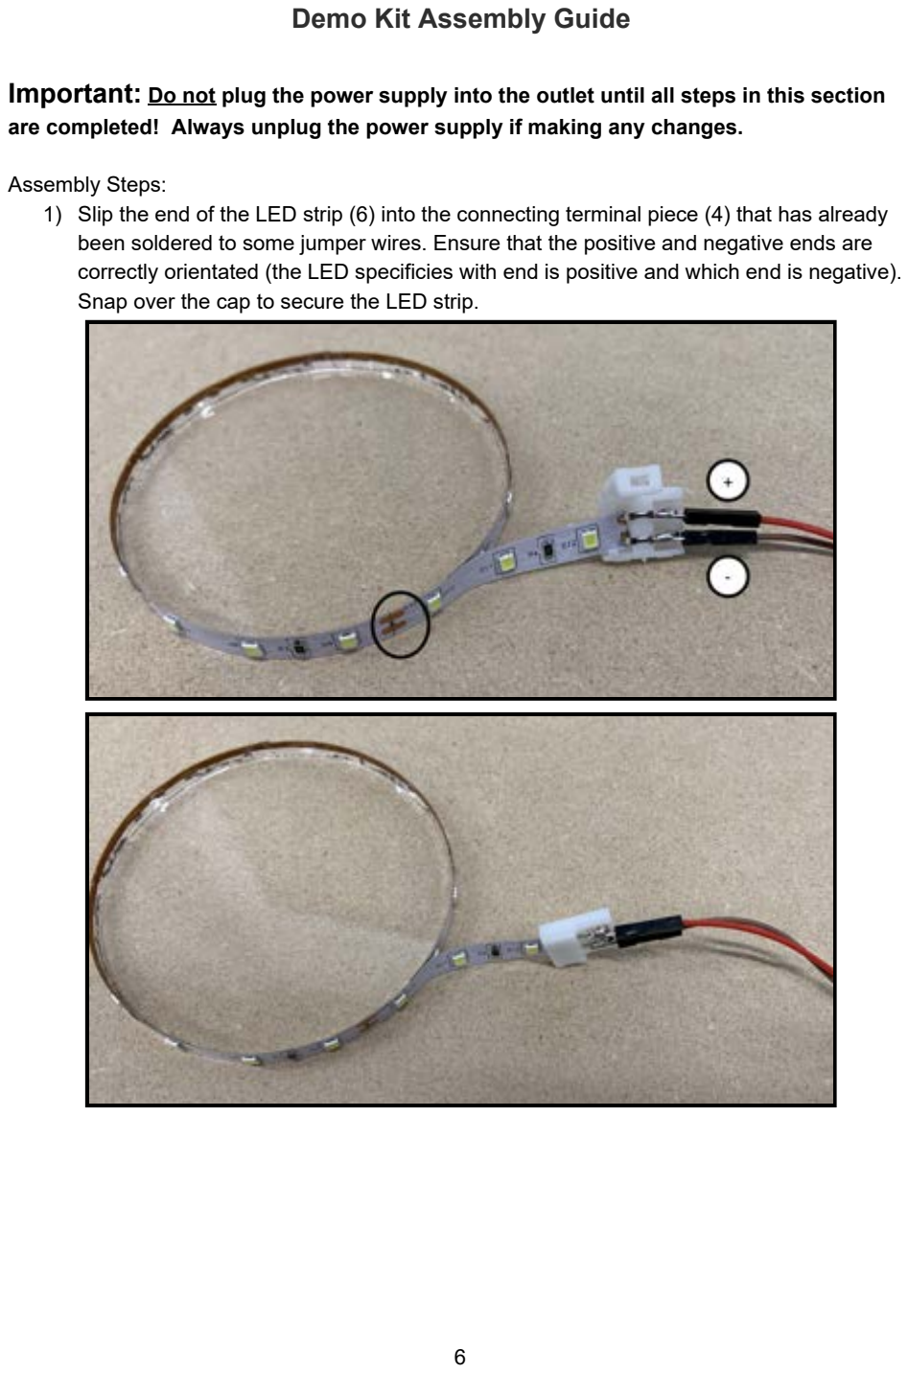
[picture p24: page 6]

Important: Do not plug the power supply into the outlet until all steps in this section are completed! Always unplug the power supply if making any changes.

Assembly Steps:
1) Slip the end of the LED strip (6) into the connecting terminal piece (4) that has already been soldered to some jumper wires. Ensure that the positive and negative ends are correctly orientated (the LED specificies with end is positive and which end is negative). Snap over the cap to secure the LED strip.

2) Insert the end pins of a new pair of jumper wires (5) (that are not soldered to anything) into the connector terminal of the power supply (1). Use the screwdriver (9) to secure the pins of the wires.

*Take note of the positive and negative ends for later.

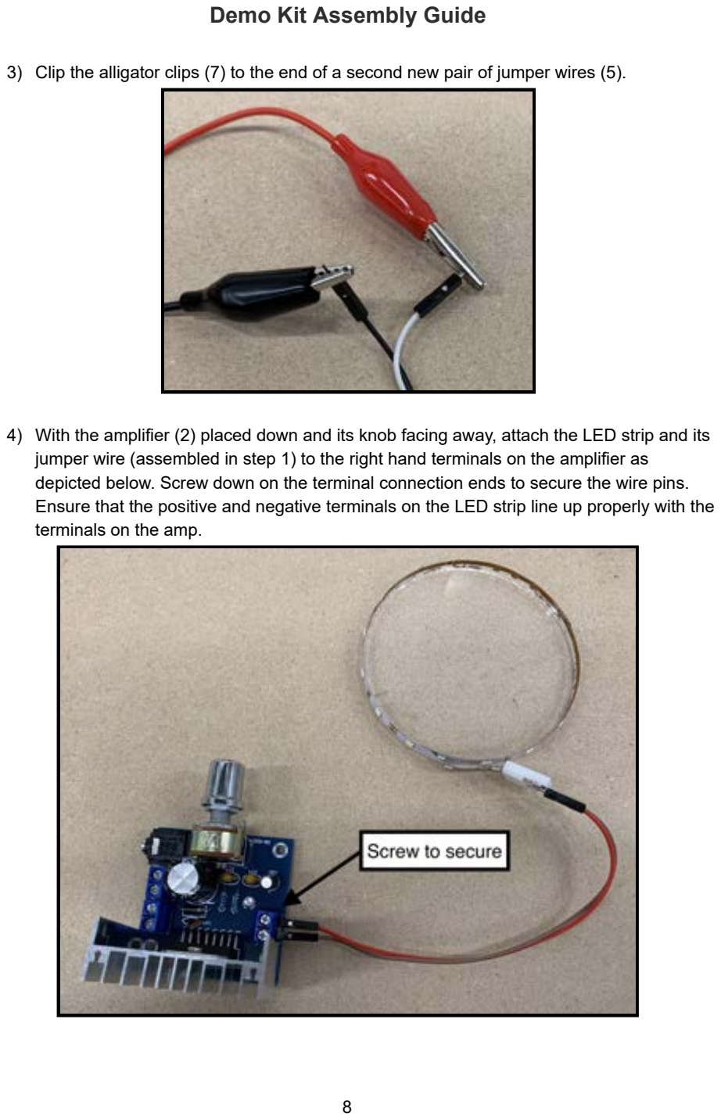
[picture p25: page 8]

3) Clip the alligator clips (7) to the end of a second new pair of jumper wires (5).
4) With the amplifier (2) placed down and its knob facing away, attach the LED strip and its jumper wire (assembled in step 1) to the right hand terminals on the amplifier as depicted below. Screw down on the terminal connection ends to secure the wire pins. Ensure that the positive and negative terminals on the LED strip line up properly with the terminals on the amp.

5) Attach the alligator clips and its jumper wire (assembled in step 2) to the left-bottom hand terminals on the amplifier. Screw down on the terminal connection ends to secure the wire pins.
6) Attach the power cord and its jumper wire (assembled in step 3) to the left-top hand terminals on the amplifier. Screw down on the terminal connection ends to secure the wire pins. Ensure that the positive and negative terminals line up properly with the terminals on the amp.

7) Attach the aux cable (3) on the top left audio jack port.

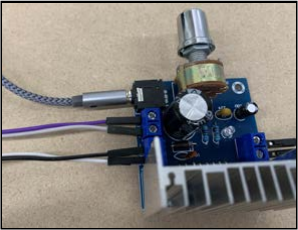
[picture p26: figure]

8) Clip the alligator clips on the two terminals on the speaker (8) being careful that the two clips do not come into contact with each other. For this step, the positive and negative terminals do not matter, so either of two configurations would work.

Final result:

## (C) User Interface

A user interface has been designed on MATLAB to drive the speaker. You will need MATLAB installed on your local machine. Here is a link to show you how to set up MATLAB on your local machine (https://ithelp.brown.edu/kb/articles/matlab-designated-computer-installation). We will control the speaker using the audio output system in your computer. We will use the ability to send different signals to the left and the right side of an audio channel and create a sinusoidal driving and a square wave for strobing simultaneously. This will allow us to control the amplitude and frequency of the strobing and driving for our set up.

1. It is important to first connect your speaker to MATLAB. The speaker ID is unique to each computer. To find out the speaker ID of your system, start MATLAB and follow the instructions.
1.1. Run the following on the command window, “ info = audiodevinfo ”
1.2. In your workspace tab, double click on the ‘info’ variable.
1.3. You will see two structured variables on your editor namely ‘input’ and ‘output’.
1.4. Double click on the output option. You will see 3 columns, ‘Name’, ‘DriverVersion’ and ‘ID’. In the name column find the connection for the speaker. It will be something like “Speaker / Headphones …” or “External …” depending on your machine. Locate the external headphones/speaker option. Obtain the corresponding ID number from the 3rd column. This ID is important to establish a connection between the speaker and MATLAB.

Here, the ID is ‘3’. Remember this ID as it will be required later.

2. Download the UI application. Navigate to the folder you have saved the application in (typically downloads folder) and start the application by double clicking the icon named “ENGN1735_2735_Vibrations_Lab_GUI”. It will take a few seconds to load. You should see the following User Interface screen load.

On the bottom right side of the screen, there is a small textfield. Enter the ID obtained in the previous section (point 1) before running the program. Note that this number might change between setups, so be sure to double check the ID each time.

3. The slider bar can be used to set the amplitude of the speaker. Note that the magnitude of the resulting speaker amplitude varies from computer to computer. The driving amplitude can be set to zero by sliding the slider to the zero position. To test if you are connected to the GUI, attach a pair of headphones to your computer using the AUX port. SET YOUR COMPUTER OUTPUT VOLUME TO ZERO AT FIRST. YOU CAN ADJUST IT LATER. We will call this the test case to check if everything works. CAUTION: IF ANYTHING GETS VERY LOUD AND UNCOMFORTABLE HIT THE “TURN OFF SYSTEM” BUTTON IMMEDIATELY. AT ANY STEP IF THERE IS AN ERROR YOU WILL HEAR THE ERROR SOUND. MAKE SURE THE SPEAKER ID ENTERED IS CORRECTLY.
4. For our first test case, we will test the connection for the GUI to send a signal to the shaker. Enter 60 Hz as the driving frequency in the text field as shown below. (This field accepts values up to 150 Hz). This is the forcing frequency for your set up. Then, slide the driving amplitude up to a value of approximately 0.05. Under the lights box, ensure that the “Off” radio button is selected. Then, press the “Turn on system” button to send a signal to your headphones. This will trigger one of the channels (left or right) of your headphones. Turn up your computer volume until a sound can be heard. Hit the “Turn off system” once an audible tone can be heard and make sure the sound stops playing.
5. REDUCE YOUR COMPUTER SYSTEM’S VOLUME TO ZERO AGAIN BEFORE RUNNING THE FOLLOWING TEST CASE. Next, we will test the connection for the GUI to send a signal to the strobing lights. Press the “On” radio button under the lights box. Then, press the “Turn on system” button again to send a signal. This will trigger a sound on the other channel of your headphones. Slowly turn up your computer's volume until an audible tone can be heard. However, do not press the “Turn off system” button. CAUTION: THIS IS A LOUD SIGNAL. IF THE AUDIO IS VERY LOUD THEN HIT THE “TURN OFF SYSTEM” BUTTON.

6. ONCE AGAIN, REDUCE YOUR COMPUTER’S VOLUME TO ZERO. Next, we will test the strobing function that will ultimately be used for the lights. Change the lights radio button from “On” to “On with Strobing”. With a very low system volume hit the “Refresh Settings Button”. This button allows for any parameters on the GUI to be dynamically updated. Once again slowly increase your computer’s audio until a sound can be heard. There are five options for strobing under the “strobing frequency” box. Choosing the “Synchronized” radio button. This will set the strobing frequency to match the driving frequency.

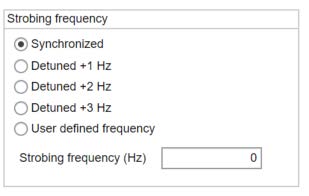
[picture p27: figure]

The second option is to have an offset strobing frequency of +1 Hz. There are additional options to increase the offset frequency to +2 Hz and +3 Hz .

\

7. The last option allows for any positive value between 0 and 150 Hz to be set as the strobing frequency, independent of the driving frequency.

Press the “Refresh Settings” button if you wish to test the other options for the offset frequency. Note that you won’t be able to hear any appreciable difference in sound, but this function’s effect will become much more evident once the lights are actually attached.

8. You can turn off the system by pressing the “Turn off system” button and the system will stop. To close the app just press the “x” on the UI window.

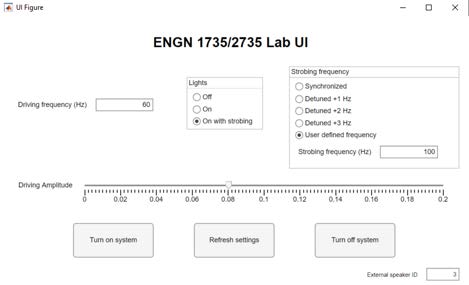
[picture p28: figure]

## (D) Testing the UI with the Speaker and Lighting

1. Attach the electronics circuit assembled in part B to the computer by inserting the AUX cable attached to the amplifier to your computer. Start the UI and enter the correct “External speaker ID.”
2. SET YOUR COMPUTER’S VOLUME TO ZERO. Keep the “Driving Amplitude” value to zero as well.
3. Turn the knob on the amplifier clockwise until it hits a stop in its rotation.
4. On the GUI, change the radio button on the lights to ‘“On”. Then, press the “Turn on system” button. Adjust the volume on your computer until the LED lights turn on and adjust the volume until the intensity of the lights are at a suitable level. Then, leave the volume on your computer fixed for the duration of the demo.
5. Next set a driving frequency of 10 Hz, and switch the Lights option to “On with strobing”. Hit refresh. You should see the lights begin to flash.
6. In very small increments, move the slider to increase the “Driving Amplitude” and hit refresh. You should see the speaker will start vibrating with a frequency of 10Hz. Ensure that the amplitude isn’t too great such that the speaker starts bottoming out (you will hear a loud rattling sound) as it could cause permanent damage. If this happens, immediately turn the volume of your computer down and restart the process.
7. Note that as you change the frequency of the signal sent to the speaker, the relationship between amplitude of the signal and the response amplitude of the speaker changes. Thus, if there is a large jump in the input frequency, it is safer to reduce the driver amplitude on the GUI before hitting refresh.

## (E) Experiments

### (1) 1 DOF and 2 DOF Assembly

Materials:

Number | Item | Quantity
1 | Housing Assembly | 1
2 | Speaker | 1
3 | Compression Springs | 2
4 | ⅜’’-16 Hex nuts | 3
5 | Custom Adapter | 1
6 | Plastic Linear Shaft | 1
7 | 8-32 Set Screw | 3
8 | 6-32 x ½’’ Hex head screw | 4
9 | 6-32 Hex nut | 4

Assembly Steps:
1) Remove the top plate of the housing assembly (1). Fasten the speaker (2) to the top plate using four 6-32 hex head screws (8) and nuts (9). Ensure that the head of the screw lies flush on the back side of the speaker.
2) Reattach the top plate of the housing now that the speaker is attached. For steps 1 and 2, review the housing assembly guide to refresh on assembling the housing plates.
10 | ¼’’-20 Hex nut (Aluminum) | 2
11 | ¼’’-20’’ Threaded Rod (Aluminum) | 1
12 | 5/64'' Allen Key | 1
13 | 7/64'' Allen Key | 1
14 | 9/64'' Allen Key | 1

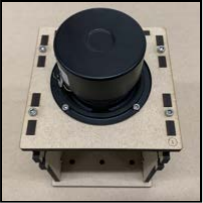
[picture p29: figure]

3) Secure the linear shaft (6) into the custom adapter (5) by inserting a 8-32 set screw (7) into the middle side of the adapter and tightening. Be careful to not overtighten. *Note that this step is optional, please only add the linear shaft if you are finding that the demo requires aligning. Otherwise, the shaft should be omitted.

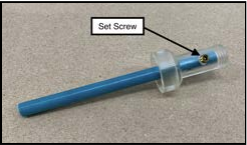
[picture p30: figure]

4) Place a ⅜’’ nut (4) on the top hexagonal slot of the custom adapter, and use two 8-32 set screws (7) to secure the nut in place.

5) Thread the ¼’’-20 aluminum rod (11) into the end of the custom adapter (5) until the rod is flush with the linear shaft (6). Secure a ¼’’-’20 aluminum hex nut (10) at the same end for a positive lock. Ensure that the ¼’’-20 rod and nut are both aluminum (there are both aluminum and steel rods given in the package). The aluminum rod and nuts are lighter in weight and are non-ferromagnetic (you can try placing the magnet around 3’’ away from the pieces to feel if an attractive force is felt).
6) For the 1DOF system, thread (twisting motion) one compression spring (3) to the hex nut attached in the custom adapter for approximately one full rotation (note that all the spring and nuts are left handed and thread in the opposite direction to traditional screws and nuts). Ensure that the compression springs aren’t threaded too deep into the nut otherwise the spring constant will be affected (limit it to one revolution). Then thread another ⅜ hex nut to the end of the compression spring. For the 2DOF system, repeat the process and add another compression spring, hex nut pair.
7) Thread the end of the spring nut assembly (steps 3-7) into the speaker (2) until the screw bottoms out, adding another ¼’’-20 nut (10) as a positive lock.

Final Results:

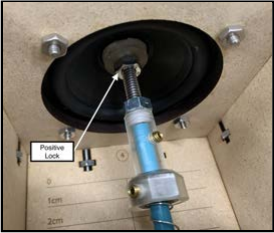
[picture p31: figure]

(1.1) Alternative assembly for use with magnet (1DOF HW): Materials:
Number | Item | Quantity | Bag Number
1 | Magnets | 2 | 5
2 | Custom mount assembly from step 6 | 1 | 1,3

1) Remove the linear threaded rod from the assembly by unscrewing the corresponding 8-32 set screw that is holding the rod.

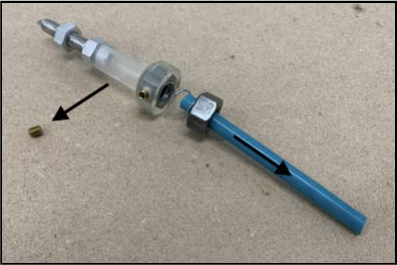
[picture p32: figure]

2) The HW1 demo assignment will ask you to test three configurations illustrated below. The first case contains the mount assembly as is. For the second configuration, attach one magnet to the end of the free nut. For the third configuration, attach another magnet on top of the previous one. Be careful to place the magnets gently on one another as they have large pull power and may be damaged if snapped together too quickly. Also ensure that the magnets are centered around the nut such that during oscillation, no side to side motion is induced.

### (2) Vibration Isolation Assembly

Materials:

Number | Item | Quantity
1 | Springs | 3
2 | ¼”-20 Nut+threaded rod | 2 (nut) 1 (rod)
3 | 8-32 x ¾” screw | 3
4 | 8-32 x 1” screw | 6
5 | 8-32 nut | 6
6 | Bottom platform | 1
7 | Speaker | 7
8 | Beans | 8
9 | ⅜’’-16 Hex nuts | 6
10 | Top acrylic plate | 1
11 | Bottom acrylic plate | 1
12 | Top platform | 1

Assembly Steps:
1) Thread the (2) ¼”-20 rod to the (6) bottom platform. Thread two of the (2) ¼” nuts to the rod.

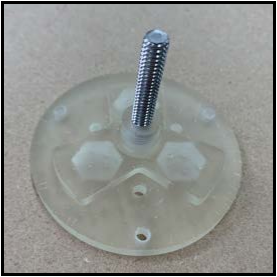
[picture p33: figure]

2) Insert three (9) ⅜’’-16 Hex nuts in the hexagonal slots on the (12) top platform.
3) Thread three (1) springs to the three (9) ⅜’’-16 hex nuts on the (12) top platform. Make sure that the springs are approximately level.

4) In order to secure the hex nuts to the platform, fasten the (10) top acrylic plate to the
(12) top platform using three 8-32 x ¾” screws.
5) Pass three (3) 8-32 x ¾” screws through the holes on the (11) bottom acrylic plate.

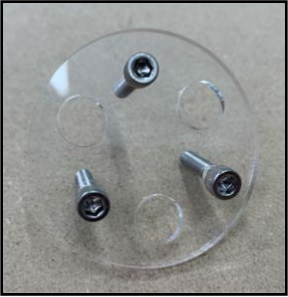
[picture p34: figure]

6) Pass the springs from step 4 through the three large holes on the (11) bottom acrylic plate such that the orientation matches the image below.
7) Thread the three remaining (9) ⅜’’-16 Hex nuts onto the ends of the spring. Make sure the nuts are approximately level with each other once threaded on. Additionally the nuts should be orientated such that they match the nuts below.

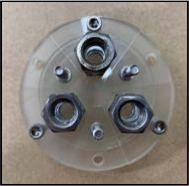
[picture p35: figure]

8) Combine the bottom platform from step 1 with the assembly from step 7 by inserting the three (9) ⅜’’-16 hex nuts into the empty hexagonal slots on the (6) bottom platform. Additionally pass the three (3) 8-32 x ¾” screws through the through holes on the (6) bottom platform.
9) Fasten the (11) bottom acrylic plate to the (6) bottom platform by using three (5) 8-32 nuts.

10) Fastening the (2) ¼”-20 rod at the underside of the bottom platform to the (7) shaker.
11) In the case where the springs need to be locked, pass three 8-32 x 1” screws through the remaining holes on the (12) top platform. Fasten the screws by threading them to the
(6) bottom platform. Sandwich a (5) 8-32 nut between the top and bottom platforms on each screw. Tighten the screw against the (12) top platform.

Final Results:

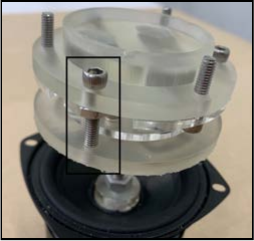
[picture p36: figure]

### (3) Nonlinear Oscillator Assembly

Materials:

Number | Item | Quantity
1 | Housing Assembly | 1
2 | L-bracket | 4
3 | Neodymium Magnet | 2
4 | Sheet Metal Strip | 1
5 | Sheet Metal Plate | 1
6 | Speaker | 1
7 | 8-32 x 1/2'' Hex head screw | 8
8 | 8-32 Hex nut | 12
9 | 6-32 x ½’’ Hex head screw | 4
10 | 6-32 Hex nut | 4
11 | ¼’’-20’’ Threaded Rod (Aluminum) | 1

*The Housing item includes all fasteners that belong to that assembly; view “(A) Housing Assembly” for more information. Assembly Steps:
1) Remove the top plate of the housing assembly. Faster the speaker to the top plate using four 6-32 hex head screws (9). Ensure that the head of the screw lies flush on the back side of the speaker. Review the housing assembly guide to refresh on the terminology used to denote specific pieces in the housing.

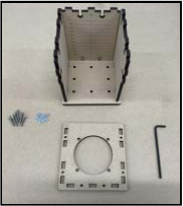
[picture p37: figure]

2) Shift the bottom plate back by one slot. Insert two L-brackets
(2) on the top and two L-brackets on the bottom. This connects the back plate to the right and left plate.
12 | ¼’’-20 Hex nut (Aluminum) | 3
13 | 9/64'' Allen Key | 1

3) Use eight 8-32 x ½’’ screws (7) and nuts to fasten the metal plate (5) to the through holes on the bottom plate. Ensure that the screw head is flush on the back surface of the bottom plate.
4) Thread the ¼’’-20 aluminum od (11) into the speaker (6). Use one ¼’’-20 aluminum hex nut (12) to fasten the rod in place. Thread a second aluminum nut just above the other.

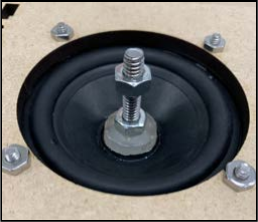
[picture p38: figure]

5) Stick the large hole on the metal strip (4) through the threaded rod, and clamp the strip in place using a third ¼’’-20 hex nut (12).
6) Mount the top panel (with the attached speaker) onto the side of the modified housing assembly (fastening with screws as previously done).

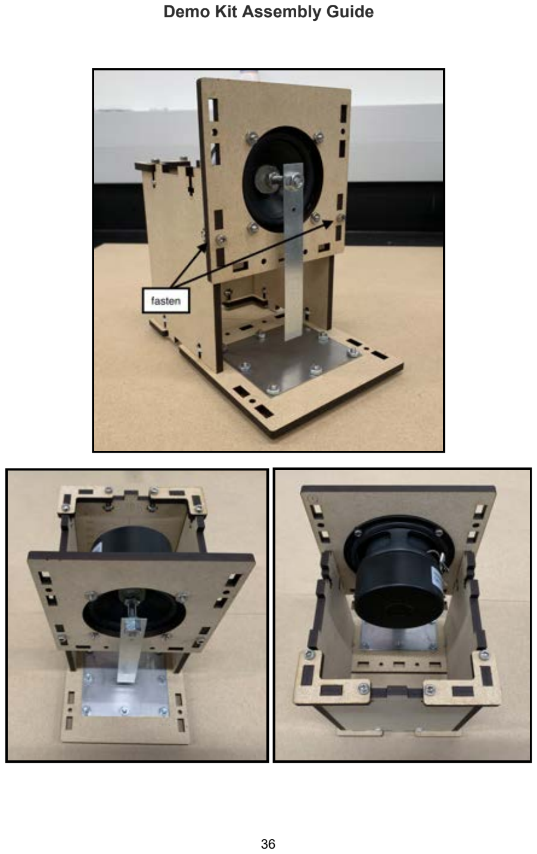
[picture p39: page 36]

7) Attach the two magnets (3) together in a side by side configuration. Attach two 8-32 hex nuts (12) to the bottom surface of the magnet. To adjust the offset height of the magnet, stack two additional hex nuts on the same surface.
One layer | Two layers
Final Results:

### (4) String-Wave Assembly

Materials:

Number | Item | Quantity
1 | Housing Assembly | 1
2 | String Mount Base Plate | 1
3 | String Mount Panel | 2
4 | String Mount Rib | 2
5 | Washer | 10
6 | String | 1
7 | T-Piece | 1
8 | Speaker | 1
9 | 8-32' Hex nut | 11
10 | 8-32 x 3/4'' Hex head screw | 11
11 | 6-32 x ½’’ Hex head screw | 4
12 | 6-32 Hex nut | 4

Assembly Guide:
1) Remove the top plate of the housing assembly. Faster the speaker to the top plate using four 6-32 hex head screws. Ensure that the head of the screw lies flush on the back side of the speaker. Review the housing assembly guide to refresh on the terminology used to denote specific pieces in the housing.

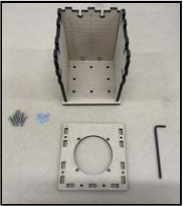
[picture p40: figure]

2) Reattach the top plate of the housing now that the speaker is attached.
13 | ¼’’-20 Hex nut (Aluminum x2, Steel x3) | 5
14 | ¼’’-20’’ Threaded Rod (Aluminum x1, Steel x1) | 2
15 | 9/64'' Allen Key | 1
16 | 7/64'' Allen Key | 1

3) Insert two of the mounting ribs (4) into the string mount panel (3) slots. The string mount plate is marked with a number 7.
4) Then, insert this assembly (step 3) into the string mount base plate (2). The base plate is marked with a number 6.

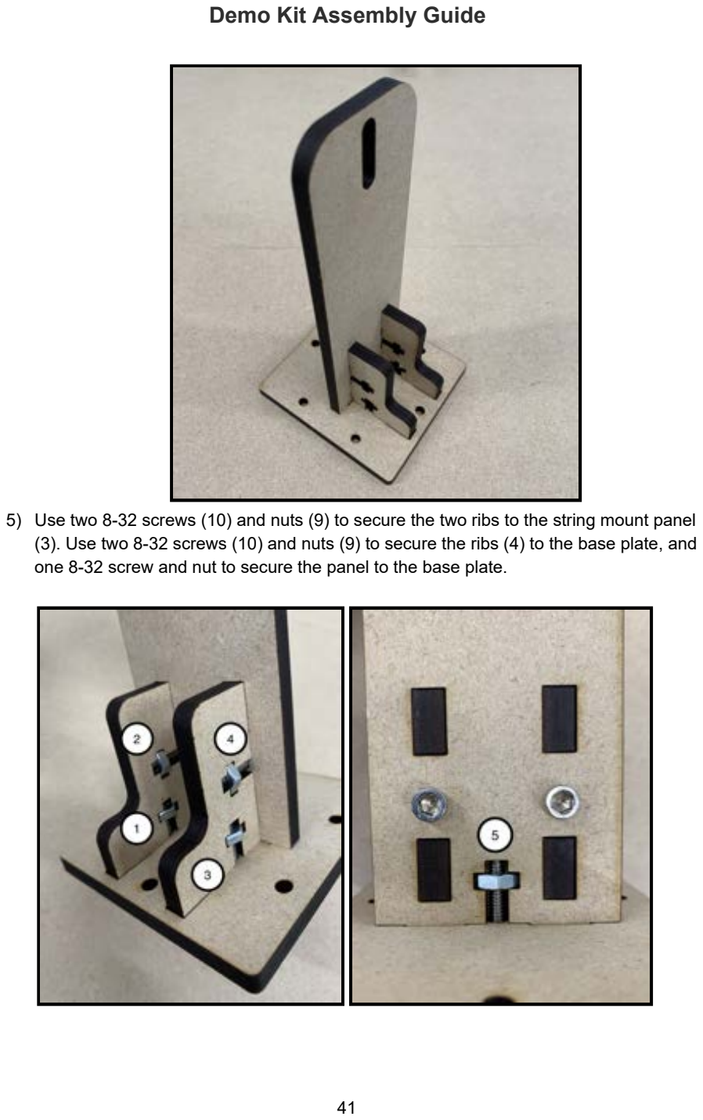
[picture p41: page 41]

5) Use two 8-32 screws (10) and nuts (9) to secure the two ribs to the string mount panel (3). Use two 8-32 screws (10) and nuts (9) to secure the ribs (4) to the base plate, and one 8-32 screw and nut to secure the panel to the base plate.

6) Insert six additional pairs of 8-32 screws (10) and nuts (9) to the peripheral holes on the base plate. Ensure that the screw head is flush at the bottom of the base plate. Tighten the nuts.

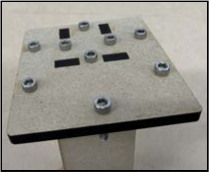
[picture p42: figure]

7) Clamp a ¼’’-20 steel rod (14) through the slot on the string mount panel (3) using two ¼’’-20 steel hex nuts (13).
8) Thread the string (6) through the top hole of the T-piece (7) and tie a double knot to ensure the string does not untie. Slide washers (5) through the string and onto the T-piece.

9) Thread three aluminum nuts (13) onto a ¼’’-20 aluminum rod (14). Tie a knot between two of the nuts. Screw the nuts together to clamp down on the string (6).
10) Thread the other end of the rod (assembled in step 9) into the speaker (8). Hang the T-piece (7) over the rod on the string mount panel (3). Move the housing and string mount apart until the T-piece and washer are suspended from the base and the string is tensioned. Slide the rod on the string mount along its slot in order to level the string.

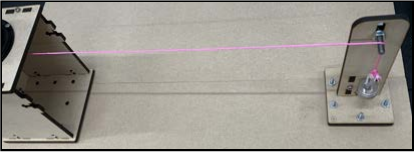
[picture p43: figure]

*Add weights onto the string mount or tape it to the ground to prevent movement as the speaker vibrates.

## (F) Manufacturing Steps

(i) Tapping 3D printed pieces:

a. Use a ¼-20” tap to rethread the bottom section of the custom adapter.
b. Use a 8-32” tap to rethread the side and central portions of the custom adapter.

c. Use a 8-32” tap to rethread three outer holes of the top and bottom platforms.
d. Use a ¼-20” tap to rethread the underside of the bottom platform.

(ii) Shaker construction:

a. Cut off the dust cap on the shaker to expose the voice coil.
b. 3D print the threaded cylindrical attachment piece (labeled “ ”) and epoxy half of it full body length to the inner edge of the voice coil.
i. Use a threaded rod to manually keep the cylindrical attachment piece in place and to ensure that it remains perpendicular to the ground.

(iii) Sheet metal construction

a. Using a hand or floor shear, cut out the outer profile of the metal strip and plate according to the dimensions provided in the engineering drawings above. The metal plate and strip should be manufactured out of 1/32” and 1/64” sheet metal respectively.

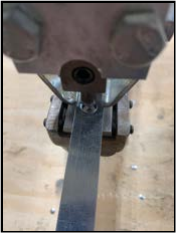
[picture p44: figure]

b. Using hole punches, cut through holes in the metal plate and strip according to the dimensions provided in the engineering drawings.

### Appendix: Full BOM

Item | Quantity | Manufacturing
⅜’’ Hex nut | 6 | NA
Compression Spring | 3 | NA
8-32 set screw | 3 | NA
Linear Shaft | 1 | NA
3D Printed Custom Adapter | 1 | 3D Printing
8-32 x ¾’’ Hex head screw | 23 | NA
8-32 x ½’’ Hex head screw | 8 | NA
8-32 Hex nut | 23 | NA
6-32 x ½’’ Hex head screw | 7 | NA
6-32 Hex nut | 4 | NA
¼’’-20 Threaded rod (aluminum) | 1 | NA
¼’’-20 Threaded rod (steel) | 1 | NA
¼’’-20 Hex nut (aluminum) | 3 | NA
¼’’-20 Hex nut (steel) | 2 | NA
Small washer | 6 | NA
Large washer | 10 | NA
5/64’’ Allan key | 1 | NA
7/64’’ Allan key | 1 | NA
9/64’’ Allan key | 1 | NA
Mini screwdriver | 1 | NA
Top platform (vibration isolation) | 1 | 3D Printing
Bottom platform (vibration isolation) | 1 | 3D Printing
Top acrylic plate (vibration isolation) | 1 | Laser Cut-¼” Acrylic

Bottom acrylic plate (vibration isolation) | 1 | Laser Cut-¼” Acrylic
T piece (string demo) | 1 | Laser Cut-¼” Acrylic
String | 1 | NA
Top Plate (1) | 1 | Laser Cut-¼” Particle Board
Left Plate (2) | 1 | Laser Cut-¼” Particle Board
Right Plate (3) | 1 | Laser Cut-¼” Particle Board
Back Plate (4) | 1 | Laser Cut-¼” Particle Board
Base Plate (5) | 1 | Laser Cut-¼” Particle Board
String Mount Base Plate (6) | 1 | Laser Cut-¼” Particle Board
String Mount Panel (7) | 1 | Laser Cut-¼” Particle Board
String Mount Rib | 2 | Laser Cut-¼” Particle Board
L-bracket | 4 | Laser Cut-¼” Particle Board
Sheet Metal Strip | 1 | Sheet Metal-1/64”
Sheet Metal Plate | 1 | Sheet Metal-1/32”
Magnets | 2 | NA
12V Power Supply | 1 | NA
Amplifier | 2 | NA
Aux Cable | 1 | NA
Jumper Wire (with LED strip connector) | 1 | NA
Jumper Wires | 4 | NA
LED Lights | 1 | NA
Acrylic disk (for LED) | 1 | Laser Cut-¼” Acrylic
Alligator Clips | 2 | NA
Speaker | 1 | NA
Cylindrical Attachment (for speaker) | 1 | 3D print

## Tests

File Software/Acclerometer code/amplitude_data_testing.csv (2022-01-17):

Frequency (Hz) | Amplitude (mm)
62.832 | 0.0089625
125.66 | 0.001966
188.5 | 0.00090307
251.33 | 0.00065524
314.16 | 0.00038848
376.99 | 0.00026778
439.82 | 0.00018745
502.65 | 0.00013332
565.49 | 9.70E-05
628.32 | 7.29E-05
691.15 | 5.58E-05
753.98 | 4.33E-05
816.81 | 3.48E-05
879.65 | 2.78E-05
942.48 | 2.32E-05

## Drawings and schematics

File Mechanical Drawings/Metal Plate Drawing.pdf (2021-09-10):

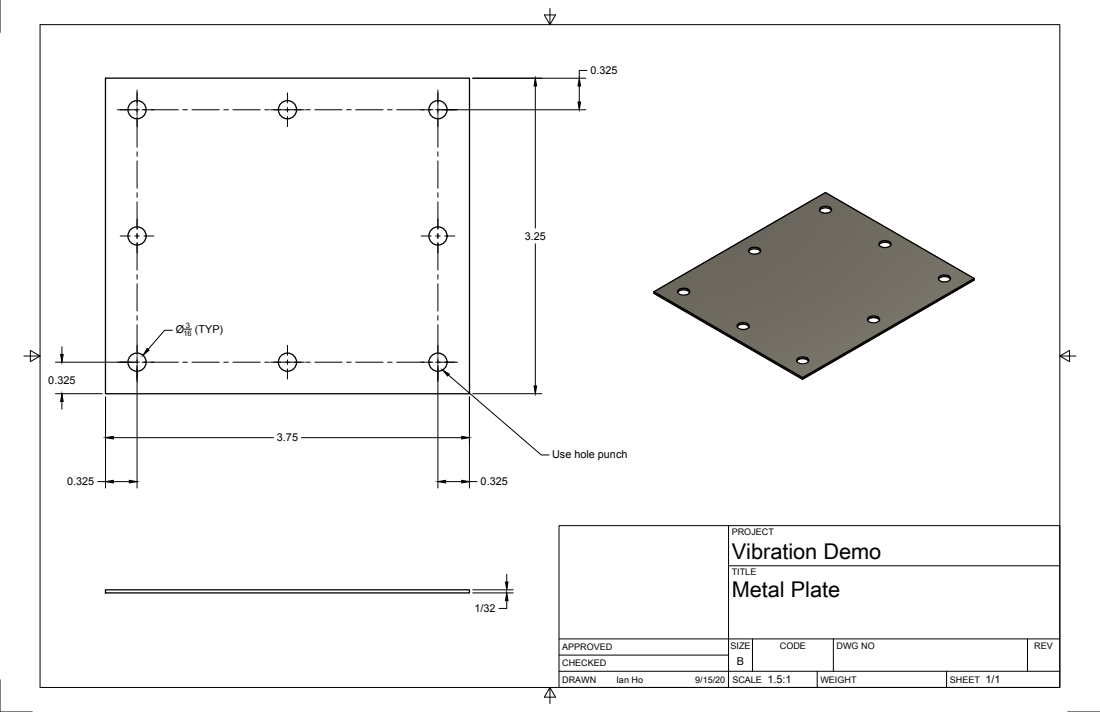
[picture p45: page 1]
SIZE; CODE; DWG NO; REV; Ian Ho; Vibration Demo Metal Plate; 16 (TYP)

Use hole punch

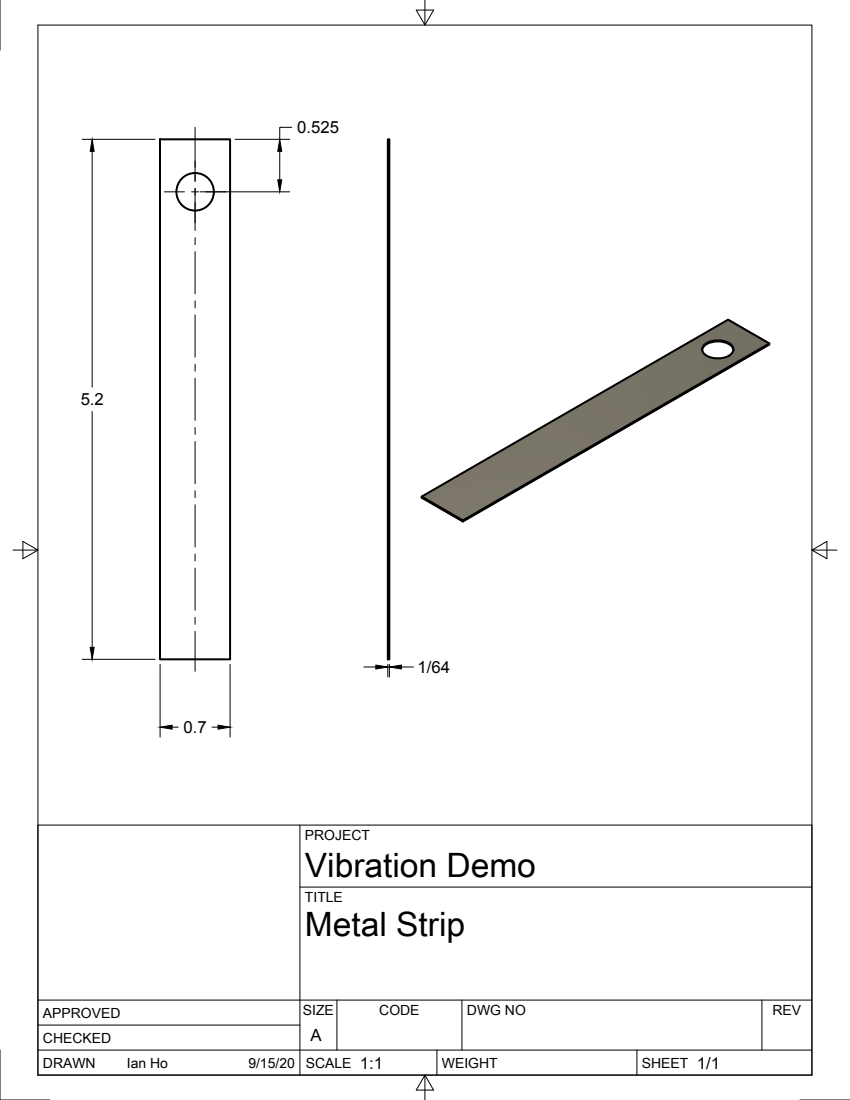
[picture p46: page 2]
SIZE; CODE; DWG NO; REV; Ian Ho; Vibration Demo Metal Strip

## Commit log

2022-01-11 Rename CAD files/1DOF:2DOF/Custom Mount to CAD files/1DOF,2DOF/Custom Mount
2022-01-18 Delete Vibration Kit Assembly Guide.pdf
    Older version replaced.
